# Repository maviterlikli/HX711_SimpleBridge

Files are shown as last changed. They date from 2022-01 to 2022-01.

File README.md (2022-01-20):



<!-- PROJECT SHIELDS -->
<!--
*** I'm using markdown "reference style" links for readability.
*** Reference links are enclosed in brackets [ ] instead of parentheses ( ).
*** See the bottom of this document for the declaration of the reference variables
*** for contributors-url, forks-url, etc. This is an optional, concise syntax you may use.
*** https://www.markdownguide.org/basic-syntax/#reference-style-links
-->
<!-- 
[![Contributors][contributors-shield]][contributors-url]
[![Forks][forks-shield]][forks-url]
[![Stargazers][stars-shield]][stars-url]
[![Issues][issues-shield]][issues-url]
[![MIT License][license-shield]][license-url]
[![LinkedIn][linkedin-shield]][linkedin-url]
-->

<!-- PROJECT LOGO 
<br />
<div align="center">
  <a href="https://github.com/othneildrew/Best-README-Template">
    <img src="images/logo.png" alt="Logo" width="80" height="80">
  </a>

  <h3 align="center">Best-README-Template</h3>

  <p align="center">
    An awesome README template to jumpstart your projects!
    <br />
    <a href="https://github.com/othneildrew/Best-README-Template"><strong>Explore the docs »</strong></a>
    <br />
    <br />
    <a href="https://github.com/othneildrew/Best-README-Template">View Demo</a>
    ·
    <a href="https://github.com/othneildrew/Best-README-Template/issues">Report Bug</a>
    ·
    <a href="https://github.com/othneildrew/Best-README-Template/issues">Request Feature</a>
  </p>
</div>
-->

<!-- TABLE OF CONTENTS 
<details>
  <summary>Table of Contents</summary>
  <ol>
    <li>
      <a href="#about-the-project">About The Project</a>
      <ul>
        <li><a href="#built-with">Built With</a></li>
      </ul>
    </li>
    <li>
      <a href="#getting-started">Getting Started</a>
      <ul>
        <li><a href="#prerequisites">Prerequisites</a></li>
        <li><a href="#installation">Installation</a></li>
      </ul>
    </li>
    <li><a href="#usage">Usage</a></li>
    <li><a href="#roadmap">Roadmap</a></li>
    <li><a href="#contributing">Contributing</a></li>
    <li><a href="#license">License</a></li>
    <li><a href="#contact">Contact</a></li>
    <li><a href="#acknowledgments">Acknowledgments</a></li>
  </ol>
</details>
-->

<!-- ABOUT THE PROJECT -->
## About The Project

<!-- [![Product Name Screen Shot][product-screenshot]](https://example.com) -->

This is a simple PCB that is designed to work with commonly found HX711 Arduino module. So, this is an extension to the original HX711 module shown below.

This is still under work. Design is finished. However, I am still writing the manual. As you can see, even for first grade electronical engineering students, there is nothing hard or important about this repo, since this is a simple Wheatstone bridge for HX711 module. However, while I work in my university, several students from computer sciences and engineering departments required a simple Wheatstone bridge for strain gauge applications. This was a design for a really primitive strain reader. It will not be useful in data acquisition applications, but it will help you learn if you are a new starter to strain gauge applications. It will, also, give you a great trick to easily calibrate your system or readings. A calibration that does not only calibrates the IC, but calibrates the whole system.

<b>Why do you need a PCB when you can do new-starter-things on breadboard?</b>

Since Wheatstone bridges are highly sensitive, it is impossible to acquire data on breadboards. If you like to see why, build a Wheatstone bridge on breadboard with any 24bit ADC and softly blow on the breadboard. The readings will go crazy. Also, any use of standard breadboard jumpers will have the same effect. This SIMPLE one sided PCB is to minimize such environmental effect. 

<b>BE CAREFUL!</b>
<br>
This PCB is designed to work with HW-27 Arduino module. However, it will work for the modules that has the same "J1" (see picture below) pin configuration.

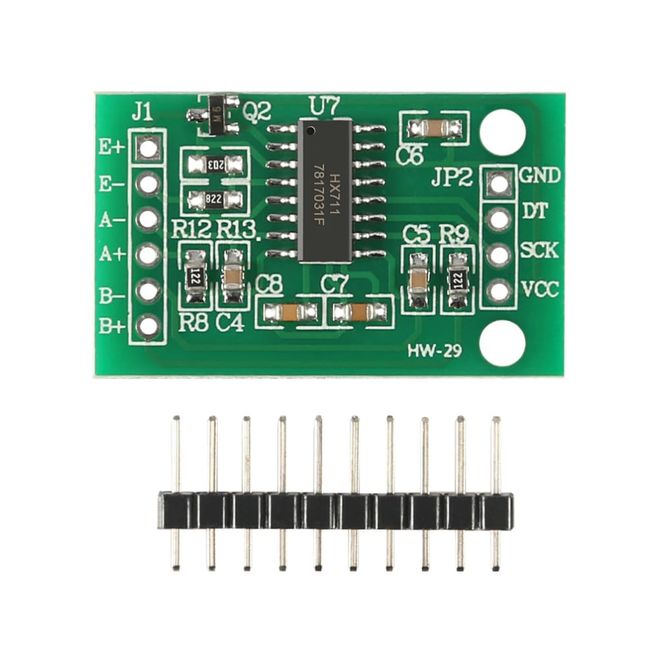
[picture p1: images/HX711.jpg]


<p align="right">(<a href="#top">back to top</a>)</p>

### Built With

The design and schematics are made in Eagle. I aim to add universal data packages as well. However, if you would like to change the dimensions, packages, or anything else, Eagle is a free software right now.

* [Eagle](https://www.autodesk.com/products/eagle/free-download)

<p align="right">(<a href="#top">back to top</a>)</p>

<!-- GETTING STARTED -->
## Getting Started

There are several ways to use the PCB. It mainly depends on your budget and required output quality. NO DOT FORGET that HX711 is not an IC that a medium or advanced strain reader can be designed from. With that in mind, if you want to use the bridge, you can simply produce it however you want, but do not spend too much money on this. 

If you are going to use HX711 with load cells, this is not for you. This repo is basically for an adapter to use strain gauges with HX711. A simple extension.

If you are going to use strain gauges and would like to read the ADC data with HX711, please do continue.

After this point, every value, name or component will be refered to the following image, if otherwise not stated. Take the image as reference. 
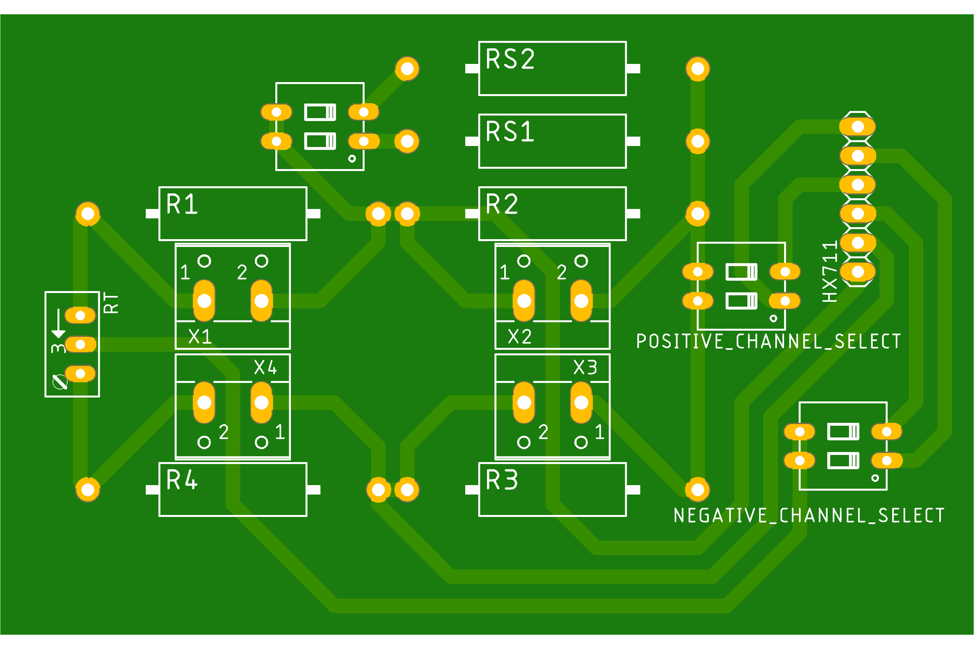
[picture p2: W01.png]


### Prerequisites

First of all, you need to know basics of Wheatstone bridge, and calculations. If you do not know where to start, HBM provides a good start-up knowledge [here](https://www.hbm.com/en/7163/wheatstone-bridge-circuit/). If you already have another source, you can use that as well, but be careful of resistor names, excitation points and reading points. They will vary.

You are required to know how ADC output works. It is simply a bit value converted to decimal, which has the maximum decimal value as maximum voltage and minimum decimal value as your minimum voltage. Maximum and minimum decimal values are dependent on your ADC bit resolution. For HX711, in data sheet it is given as "The output 24 bits of data is in 2’s complement format. When input differential signal goes out of the 24 bit range, the output data will be saturated at 800000h (MIN) or 7FFFFFh (MAX), until the input signal comes back to the input range"
So;

800000h will be equal to -8388608

7FFFFFh will be equal to +8388607 in decimal.
### Choosing the Strain Gauge

In here, if you already have a strain gauge, use that. However, if you do not have any strain gauges, there are 3 ohm values: 120, 350, 1000 ohms. Choose as you like, but remember you will need to buy resistors according to those values. So be careful if you will be able to supply resistors.

Quality of the strain gauges is totally up to your budget. If this is your first time, buy the cheap ones. However, be careful to get EXACT gauge factor. Without exact factor, you can not convert ADC readings to meaningful strain values. This value is not SAME all over a single product from a single factory. High end suppliers measure and give exact strain gauge factor for every batch of gauges.

You will require following resistors for following strain gauge resistance values. 

Assuming quarter-bridge configuration with trimpot as zero-balancer;

| Strain Gauge  | Required Resistors | Required TrimPots|
| ------------- | ------------- | ------------- |
| Ohm  | NumberofResistorsxOhm | NumberofTrimpotsxOhm |
| 350 Ω  | 3x330   | 1x50 |

Secondly, how we calculate the resistor values is this. Assume R2 to be your strain gauge, so 120 Ω, 350 Ω or 1000 Ω. For the PCB above, <b>(R4+RT/2)/(R1+RT/2)</b> should be equal or really close to <b>R2/R3</b>. In here, if you have a really minor imbalance, it can be corrected by trimpot. You can decide your resistor values like this, or you can use my implementation, which will be based on 350 Ω stain gauges and most common resistor values. BE CAREFUL your choose of resistors will effect the output. So you may need to do more calculations.

So, if we chose 350 Ω strain gauge, and 330 Ω commonly found resistors for R1, R3 and R4, as a trimpot 50 Ω for RT, and set the trimpot to divide resistance 36 Ω to 14 Ω (which 36 Ω should be added serially to R1) system ALMOST balances. So balance equation becomes;
| Left Side  | Right Side |
| ------------- | ------------- |
| 1.063953488  | 1.060606061  |

Remaining unbalance can be corrected with trimpot easily.

<b> As a final important note, DO NOT USE</b> your strain gauges without properly gluing it to a proper reading surface. Strain gauges consists of a thin backing layer, which will not stand usage on their on. Find a piece of metal, plastic or anything, apply the strain gauge with a proper and strong adhesive, use strain gauge terminal to increase the cable dimension, and make sure your cables are not going to rip off. It is really easy to damage the cables of strain gauge.

### Choosing Bridge Structure
In here, the first thing you need to know is if you are going to need a manual way to zero balance the bridge. This depends on several things like resistor tolerances, ADC gain (PGA) and required reading range. Simply, if you are using high gain with high tolerances, your zero reading may be off scale already. In that case, your system will not work at all.

So, if you are using %5 tolerance resistors with the implementation given in the <b>Choosing the Strain Gauge</b> topic, due to resistor tolerances, there can be up to 0.25 V initial imbalance. However, at the largest reading range, (5 V excitation, 32 gain) HX711 will read voltages between +0.078125 V and -0.078125 V. As you can see, the resistor tolerances will shift your output to out of range. This is why a trimpot is used in the system to zero-balance the bridge.

The only case you can implement the given bridge without trimpot is if you have 0.1% tolerance resistors which are quite expensive. It would not be logical to dump so much money into a system of this quality. So, if you do not know better, use trimpot to zero balance the system, so you can use cheap solutions. Also, in this tolerance calculation, resistance of PCB pathways are neglected. If you include pathway resistances, tolerances, and PCB quality becomes much tighter, meaning even more expensive.

So, if you use 

330 Ω resistors for R1, R3 and R4,

350 Ω strain gauge for R2,

and 50 Ω trimpot for RT

you will make the bridge work. However, this implementation will make things a bit harder later on, in calibration, but it will be nothing that a little math cannot solve.

### Choosing Shunt Calibration Resistors
Shunt calibration resistors are used to apply a virtual strain to the system. Since the applied values of resistors are known and output can be obtained, system can be calibrated. [There](http://www.vishaypg.com/docs/11064/tn514.pdf) is an excellent guide on how to use and calculate shunt calibration. In this implementation, I am going to use 2 resistors, since we have much higher tolerances and not so sensitive bridge. Choosing the resistor values depends on your reading range. It is better to apply higher strains, which means lower resistor values on shunt calibration. However, it cannot exceed the reading range of the ADC. So ideally, if you apply 10 kΩ parallel resistor to system (as RS1 or RS2) you will cause 0.043005 V shift in ADC reading. Since 32 gain measures voltages between +0.078125 V and -0.078125 V, this will work. However, 128 gain and 64 gain will have a reading range of ±0.01953125 V and ±0.0390625 V, respectively. 10 kΩ shunt calibration resistors will not work for 128 and 64 gain, since it will shift the value out of range. 

<b> If you do not know which gain you are going to use, 50 kΩ and 100 kΩ shunt calibration resistors will work fine.</b>

<p align="right">(<a href="#top">back to top</a>)</p>

### List of Components
To use my implementation with 350 Ω strain gauges, you will need;

- 3 x 330 Ω resistor (prefer metal film, or as low tolerance as can be)
- 1 x 50 Ω trimpot (prefer as much turn as possible. Usually I use 20 turn)
- 1 x 2 pin connector (to your preference)
- 3 x DIP Switch
- 1 x 50 kΩ resistor for RS1
- 1 x 100 kΩ resistor for RS2

<p align="right">(<a href="#top">back to top</a>)</p>

### Preliminary Measurements
This step is the most important step. To have a proper measurement, you have to know your resistor values. You can use a simple multimeter, or anything more advanced. My procedure is as follows;
1. Measure R1, R3, R4 and RT, and SAVE them somewhere you will not misplace.
2. (optional) If you want more precision, you can measure the PCB pathway resistances and add them to proper resistor values. 
3. ONLY solder the RS1, RS2 and DIP switch that connects shunt calibration resistors to the main bridge. 
4. Measure the resistor values at the ends of RS2 (be careful R2 should not be soldered yet, or any other components.) in 3 possible states and SAVE them somewhere you will not misplace. 3 possible states are;
    - switch1 (RS1) on, switch2 (RS2) off
    - switch1 (RS1) off, switch2 (RS2) on
    - switch1 (RS1) on, switch2 (RS2) on
5. You can now solder the remaining parts.

<p align="right">(<a href="#top">back to top</a>)</p>

### Soldering

It is assumed that the PCB is one sided and components are on the other face of the copper layer. However, since all the components are passive, you can switch sides, except HX711 pins.

BE CAREFUL to follow soldering order given in <b>Preliminary Measurements</b> to obtain best results.

There are 2 elements to every component at a Wheatstone bridge, a resistor and a connector. Connector is to add strain gauge to system, and resistors are static components. So, if you are going to use quarter-bridge, DO NOT solder X1, X3 and X4 connectors, but solder R1, R3 and R4 resistors. To add the strain gauge, DO NOT solder R2 resistor, but solder X2 connector. For other bridge implementations, logic is same. So, you eighter use a connector or a resistor.

## Calibration

If you are going to calibrate the system with any other method, or if you do not require a calibration, you may skip this step. But if you need calibration, we will conduct a Ax+B calibration.

To do so, it is required to know shunt calibration resistor values, bridge resistor values and virtual strain that is applied by shunt calibration resistors. Assuming R1, R3 and R4 to be static, 

Epsilon_s = -R_G/(F_G*(R_G+R_S))

where;

Epsilon_s   : Strain on the strain gauge (m/m)
R_G         : Strain gauge resistance value (Ω)
R_C         : Shunt calibration resistor value (Ω)
F_G         : Strain gauge factor (must be given by supplier)

By conducting the calculation for every state of RS1 and RS2 switch, you will have 3 strain values and 3 outputs from the ADC. You do not have to but you can also add your zero reading (not perfectly zero) to this data set, which makes 4 strain values and 4 ADC outputs (given as Parameters in <b>Usage</b>). Only remaining thing is to linearly convert ADC values to match strain values. 
1. First thing I suggest you to do is a check of system. To do that, take your readings (4 state of switch (R_G), 4 ADC output) and calculate linear regression error. As an alternative, you can use Microsoft Excel (or any other related software) draw the diagram of data as scatter graph, then make Excel to calculate equation and R^2 value. If your R^2 value is really close to 1, you have a good working system.
2. By applying the calculations above, you should have 4 strain values (Epsilon_s).
3. Take the values from ADC output that are designated as <b>Parameter: ADCout0, ADCout1, ADCout2, ADCout3 </b>
4. Make a table.

| Strain values | ADC Outputs |
| ------------- | ------------- |
| Epsilon_s=0 | ADCout0 |
| Epsilon_s RS1 | ADCout1 |
| Epsilon_s RS2 | ADCout2 |
| Epsilon_s Rs1 and RS2 | ADCout3 |

5. Calculate the number that you need to multiply and add with ADCout to match with epsilon values.

For example,
| Strain values | ADC Outputs | ADCout x A + B | Calibrated Output |
| ------------- | ------------- | ------------- | ------------- |
| 0 | 1000 |  1000 x -0.00001 + 0.01 | 0 |
| -0.01 | 2000 | 2000 x -0.00001 + 0.01 | -0.01 |
| -0.02 | 3000 | 3000 x -0.00001 + 0.01 | -0.02 |
| -0.03 | 4000 | 4000 x -0.00001 + 0.01 | -0.03 |

<b> Readings in this method are always gives results in compressive strain.</b>

## Usage
First of all, you need to select a channel, POSITIVE_CHANNEL_SELECT and NEGATIVE_CHANNEL_SELECT switches are made for that. I added this switches and I have not tested it. It is simply to direct signal to channels. This may not be necessary. If you are sure you do not need that, you can short the connections. However, if you are going to use;

If you are going to use channel A, 
- set POSITIVE_CHANNEL_SELECT, 1st to off and 2nd to on
- set NEGATIVE_CHANNEL_SELECT, 1st to off and 2nd to on

If you are going to use channel B, 
- set POSITIVE_CHANNEL_SELECT, 1st to on and 2nd to off
- set NEGATIVE_CHANNEL_SELECT, 1st to on and 2nd to off

Make sure switch of RS1 and RS2 are open (is not connected to system) (off).

Then power-up the system and take ADC readings. Turn the trimpot RT until you get a zero or near zero reading. Take a several second stable reading, take the average and save. <b>Parameter: ADCout0</b>

<b>IMPORTANT NOTE:</b> DO NOT use any code that has in-code zero function (tare). Make sure that you are seeing the direct output of the ADC

After you have your zero level; 
- Close switch that is connected to RS1, take a several second stable reading, take the average and save. <b>Parameter: ADCout1</b>
- Close switch that is connected to RS2, take a several second stable reading, take the average and save. <b>Parameter: ADCout2</b>
- Close switches that is connected to RS1 and RS2, take a several second stable reading, take the average and save. <b>Parameter: ADCout3</b>
- 
<b> While calibrating, DO NOT change the strain of the material your strain gauge is placed. Make sure there are no external loads on measured part.</b>
<b> While closing and opening switches, please wait for system to converge.</b>

After this step, open the switches of RS1 and RS2. Now, you are ready to take your strain reading. In this method, you will convert your readings into meaningful strain values after you completed strain readings. However, after calculating necessary calibration values, you can input those values to your code that reads ADC as well. 

<p align="right">(<a href="#top">back to top</a>)</p>

## License

This is not licensed. You can steal it. 
<p align="right">(<a href="#top">back to top</a>)</p>

<!-- CONTACT -->
## Contact

Fahri Emre Özdemir - [@linkedin](https://www.linkedin.com/in/fahriemreozdemir/)

Project Link: [HX711_SimpleBridge](https://github.com/maviterlikli/HX711_SimpleBridge/)

<p align="right">(<a href="#top">back to top</a>)</p>

<!-- MARKDOWN LINKS & IMAGES -->
<!-- https://www.markdownguide.org/basic-syntax/#reference-style-links -->
[contributors-shield]: https://img.shields.io/github/contributors/othneildrew/Best-README-Template.svg?style=for-the-badge
[contributors-url]: https://github.com/maviterlikli/HX711_SimpleBridge/graphs/contributors
[forks-shield]: https://img.shields.io/github/forks/othneildrew/Best-README-Template.svg?style=for-the-badge
[forks-url]: https://github.com/maviterlikli/HX711_SimpleBridge/network/members
[stars-shield]: https://img.shields.io/github/stars/othneildrew/Best-README-Template.svg?style=for-the-badge
[stars-url]: https://github.com/maviterlikli/HX711_SimpleBridge/stargazers
[issues-shield]: https://img.shields.io/github/issues/othneildrew/Best-README-Template.svg?style=for-the-badge
[issues-url]: https://github.com/maviterlikli/HX711_SimpleBridge/issues
[license-shield]: https://img.shields.io/github/license/othneildrew/Best-README-Template.svg?style=for-the-badge
[license-url]: https://github.com/maviterlikli/HX711_SimpleBridge/blob/master/LICENSE.txt
[linkedin-shield]: https://img.shields.io/badge/-LinkedIn-black.svg?style=for-the-badge&logo=linkedin&colorB=555
[linkedin-url]: https://linkedin.com/in/fahriemreozdemir
[product-screenshot]: images/screenshot.png

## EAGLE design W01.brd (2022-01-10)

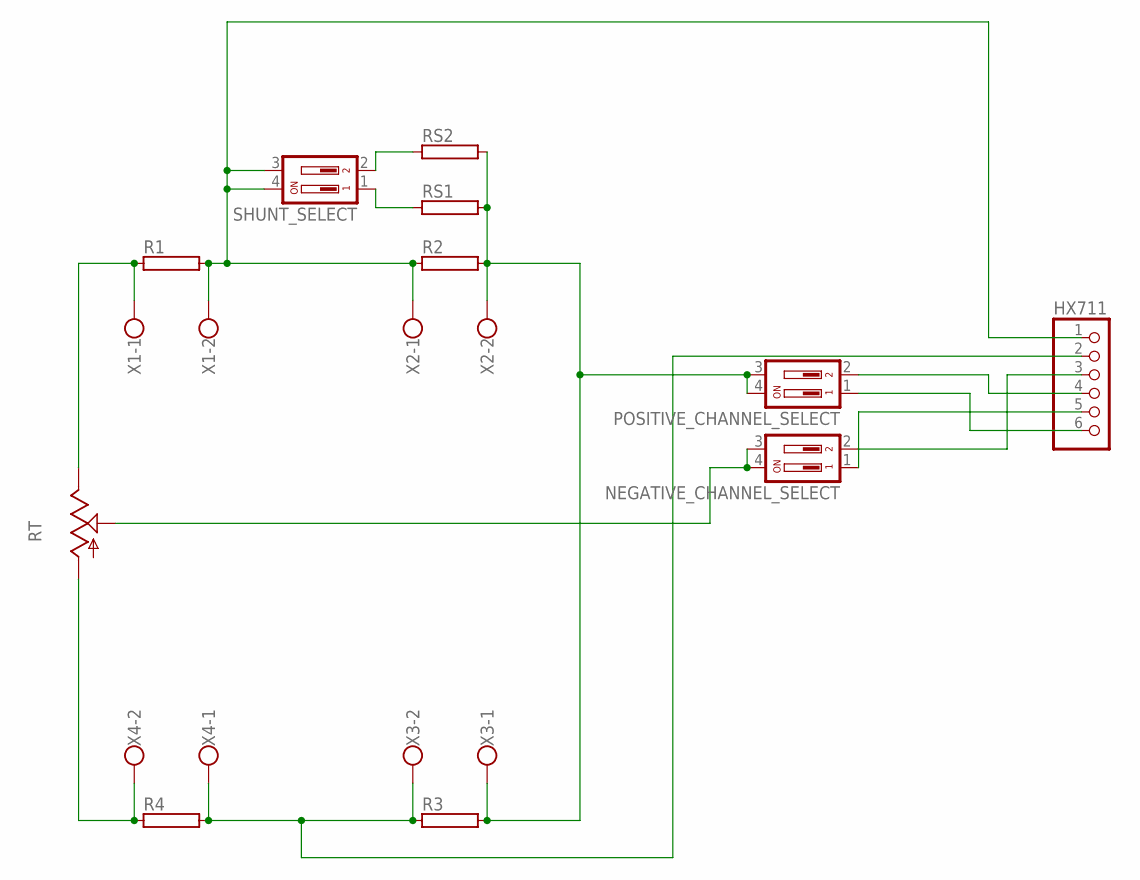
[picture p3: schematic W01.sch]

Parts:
HX711: PINHD-1X6; 1X06
NEGATIVE_CHANNEL_SELECT: DIP02YL
POSITIVE_CHANNEL_SELECT: DIP02YL
R1, R2, R3, R4: RAC03; AC03
RS1, RS2: RAC03; AC03
RT: TRIM_US-RJ9W; RJ9W
SHUNT_SELECT: DIP02YL
X1, X2, X3, X4: W237-102

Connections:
unnamed: HX711.1, R1.2, R2.1, SHUNT_SELECT.3, SHUNT_SELECT.4, X1.2, X2.1
unnamed: RS2.1, SHUNT_SELECT.2
unnamed: HX711.2, R3.1, R4.2, X3.2, X4.1
unnamed: R1.1, RT.E, X1.1
unnamed: R4.1, RT.A, X4.2
unnamed: HX711.4, POSITIVE_CHANNEL_SELECT.2
unnamed: HX711.6, POSITIVE_CHANNEL_SELECT.1
unnamed: HX711.5, NEGATIVE_CHANNEL_SELECT.1
unnamed: HX711.3, NEGATIVE_CHANNEL_SELECT.2
unnamed: POSITIVE_CHANNEL_SELECT.3, POSITIVE_CHANNEL_SELECT.4, R2.2, R3.2, RS1.2, RS2.2, X2.2, X3.1
unnamed: NEGATIVE_CHANNEL_SELECT.3, NEGATIVE_CHANNEL_SELECT.4, RT.S
unnamed: RS1.1, SHUNT_SELECT.1

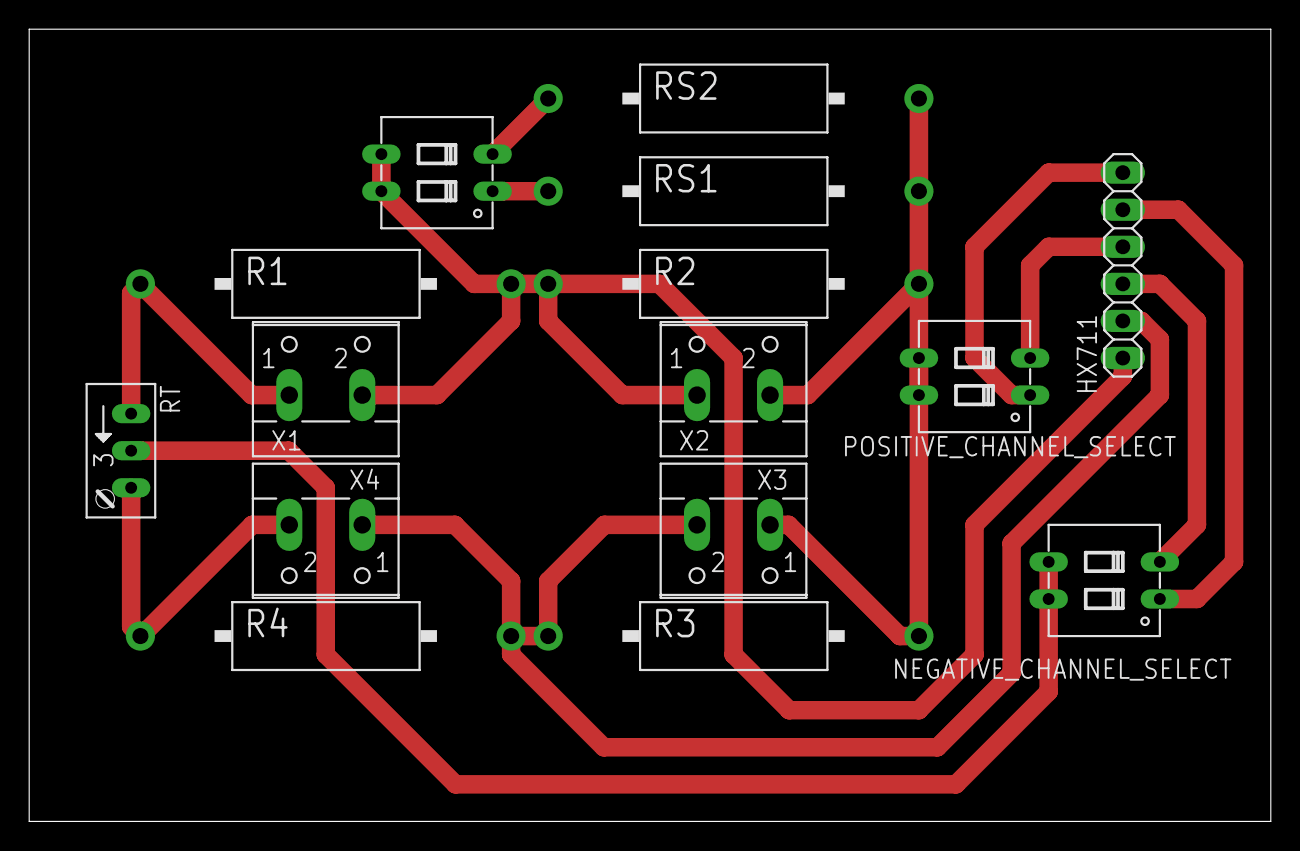
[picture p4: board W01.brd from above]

Board: 2 copper layers, 85.1 x 54.3 mm, 15 parts (0 on the bottom side), 12 nets.
